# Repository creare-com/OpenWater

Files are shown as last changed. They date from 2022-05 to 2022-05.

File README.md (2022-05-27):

# OpenWater: A Citizen Science Water Quality Monitoring Platform
The goal of this project is to provide the bill of materials, design files, electronics, and firmware to allow you to build your own research grade turbidity meter. We hope that this work will help you to evaluate water quality in your local community through education or citizen science projects.

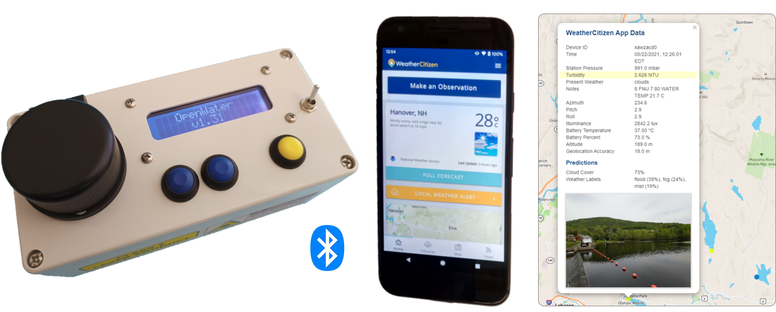
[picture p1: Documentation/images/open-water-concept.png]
OpenWater Turbidity Meter and Mobile Application


This project was supported by NOAA via SBIR contract WC133R18CN0057

## Assembly and Operation
For instructions on how to assemble, calibrate, and use the meter, see the [Documentation](https://github.com/creare-com/OpenWater/blob/master/Documentation).

## License
The Firmware is released under the BSD 3-Clause License.  The Hardware is released under the CERN Open Hardware License v2 - Permissive.  Use at your own risk.

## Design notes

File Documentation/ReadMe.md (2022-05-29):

## Documentation

**CAUTION! This project utilizes a laser diode. Read and follow all safety precautions.**

The R&D Report describes the design, validation, and testing of the turbidity meter during the project.

Follow the Assembly Instructions to build your own meter from the [parts list](https://github.com/creare-com/OpenWater/tree/main/Bill%20of%20Materials). Refer to the Operation Manual for calibration and safe operating instructions.

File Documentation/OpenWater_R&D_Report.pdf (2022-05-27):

OPENWATER – A CITIZEN SCIENCE MONITORING PLATFORM
Research & Development Report

### 1 INTRODUCTION

This report describes the research and development of the third-generation version of a research quality, relatively low-cost, open-source instrument for measurement of water turbidity in environmental samples. The device is shown in Figure 1.

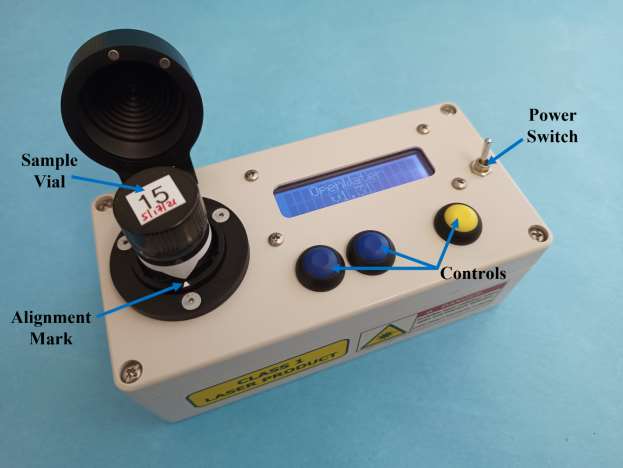
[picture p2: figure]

Figure 1. OpenWater Open-Source Turbidity Meter (3rd-Generation Design)

Principle of Operation. The OpenWater turbidity meter is composed of an 850 nm light source oriented at 90° to a light sensor which measures diffuse light scattered by turbidity in the sample. The infrared light source reduces the influence of sample color on turbidity measurements, and results are reported in Formazin Nephelometric Units (FNU). The meter was developed using guidance from Water Quality Standard ISO 7027 (Method c).

### 2 INSTRUMENT DESIGN

Design Overview. The core of the meter is the sample measurement well (Figure 2), which can be fabricated by 3D printing (stereolithography, SLA). The light source is a vertical cavity surface-emitting laser (VCSEL) with a total beam divergence angle (full-width at half intensity) of 4°. The VCSEL is operated in constant current mode to provide uniform light intensity for each measurement. The sensor is a light-intensity-to-frequency converter, which produces a square wave pulse output proportional to the incident light intensity. Pulses are counted during the integration period by a microcontroller which also controls the system.

The inner wall of the sample holder is corrugated to enhance absorption of stray light. A spring-plunger pushes the sample vial against PTFE guide rods in the wall to ensure consistent centering of the vial on the VCSEL. An alignment arrow on the top surface of the vial housing improves consistency of vial alignment. A miniature normally open reed switch placed in series with the laser is used as a safety interlock. A magnet is installed in the lid of the device to close the switch during operation, and the reed sensor is mounted in the sample holder opposite the magnet. Closing the lid actuates the reed switch, allowing the laser to be turned on by the microcontroller.

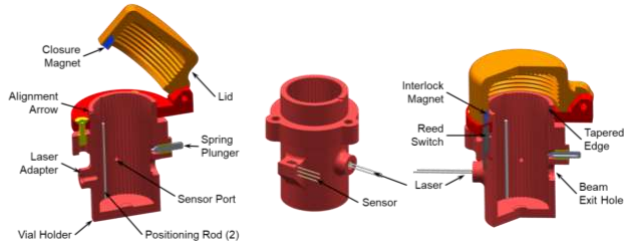
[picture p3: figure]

Figure 2. Turbidity Meter Optical System Design. The laser axis is arranged at 90° to the sensor view axis and both are normal to the vial axis. The sensor is mounted at the end of a narrow bore to minimize stray light (left); The light source and sensor are mounted directly on the outside of the sample holder (middle); The spring-plunger aligns the sample vial and laser centerlines (right).

Electronics. The VCSEL light source (TT Electronics, OPV332) is operated in constant current mode. The laser current source circuit is based on the LM-317 regulator, which has low cost, small component count, and stable current regulation. Figure 3 shows the laser control subsystem, including the laser, current regulator, reed switch safety interlock, and transistor interface to the microcontroller.

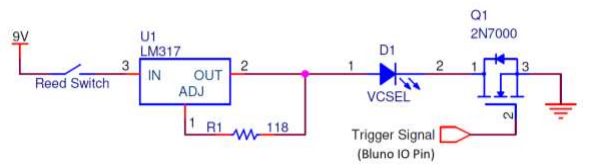
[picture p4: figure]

Figure 3. Laser Control Circuit Including Safety Interlock Reed Switch

The laser generates a repeatable signal at low turbidity values with a supply current of 10 mA. However, the voltage supplied by the microcontroller digital outputs is insufficient to drive this current. Therefore, the current source circuit is supplied with 9 V directly from the battery and the microcontroller digital output controls the laser via a 2N7000 transistor. The current source provides stable regulation with mean variability of 4.8 µA and drift between 22 and 50°C of only 0.5%.

The light-intensity-to-frequency converter (AMS, TSL237) only requires one 0.1 µF decoupling capacitor connected across the power supply. The sensor output is connected to an input pin of the 8-bit microcontroller with Bluetooth (Bluno ATmega328P, DFR0267, DFRobot) which controls the system. This board interfaces with an LCD module used for calibration and results display. Figure 4 shows the connections between the microcontroller and the low cost VCSEL and light sensor.

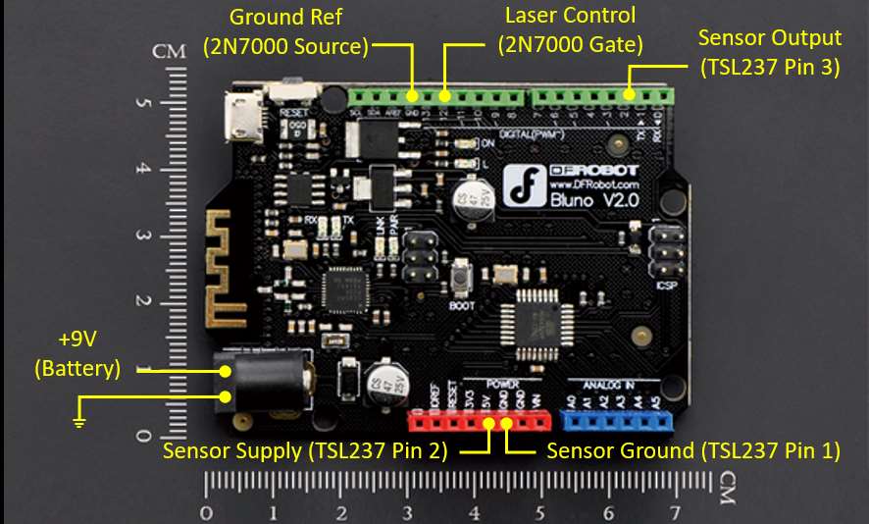
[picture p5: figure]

Figure 4. Bluno Microcontroller Connections to Light Source and Sensor

Enclosure. A commercial splash-resistant plastic enclosure (090816060, Rose Enclosures) is used for the third-generation prototype. The box measures 160 mm L x 80 mm W x 55 mm H (6.3 x 3.2 x 2.2 in.), providing ample space for the sample holder, microcontroller, LCD display, and battery pack. The lid of the enclosure is modified to accommodate the system components, as shown in the drawing in Figure 5. A piece of adhesive-backed Velcro (loop side) is installed on the inner wall of the enclosure base, opposite the laser beam exit hole in the vial holder. This simple, low-cost, absorptive material reduces the background count (light intensity measured at 0 NTU) by 30 percent and increases the ratio between counts at 0 and 20 NTU by 25 percent.

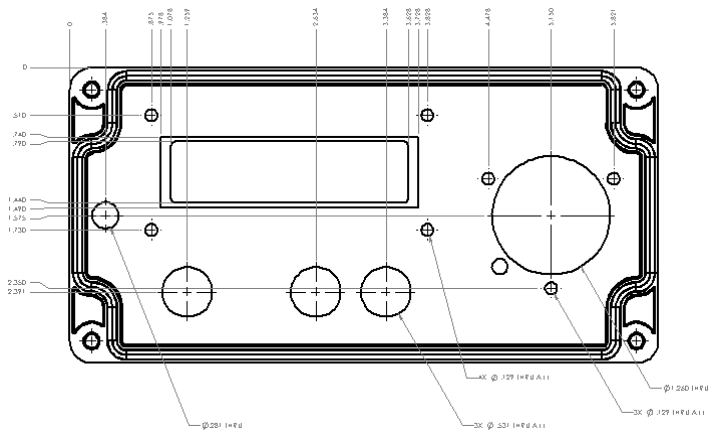
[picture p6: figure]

Figure 5. Modifications to the Commercial Enclosure

Safety. The turbidity meter contains a laser device that produces invisible radiation at 850 nm. If the laser is operated with a current greater than the recommended maximum (i.e., in an overcurrent failure mode at 30 mA), it will produce class 3B laser radiation. Class 3B devices have beams that are normally hazardous when a direct exposure occurs within Nominal Ocular Hazard Distance (NOHD). The IEC 60825-1 laser safety standard specifies an NOHD of several meters for class 3B devices.

There is no danger of harm due to the radiation from the laser in this instrument when it is used according to the instructions in the user manual. The following turbidity meter design features are meant to protect the user from potentially harmful infrared radiation:

- An interlock switch connected in series with the laser prevents operation while the lid is open.

- A warning label is placed over the seam of the enclosure to remind users not to open the enclosure while the device is powered on.
- The laser is operated in constant-current mode, below the recommended maximum current (<12 mA).
- The axis of the laser beam is oriented parallel to the base of the measurement well so that laser light is not directed towards the user.

Firmware. The OpenWater sensor uses an Arduino-type microcontroller with an integrated Bluetooth radio (Bluno, DFRobot). For the third-generation design, the system is controlled either by using buttons and an LCD display on the front panel, or via Bluetooth. In addition to the power switch, the front panel includes Up/Down buttons for scrolling through menus, and an Enter button for accepting settings (Figure 6). The calibration routine allows for selection of the integration time for each reading and the number of readings that are averaged for each measurement. The user can also select the value of each of the calibration points (typically 0 and 20 FNU).

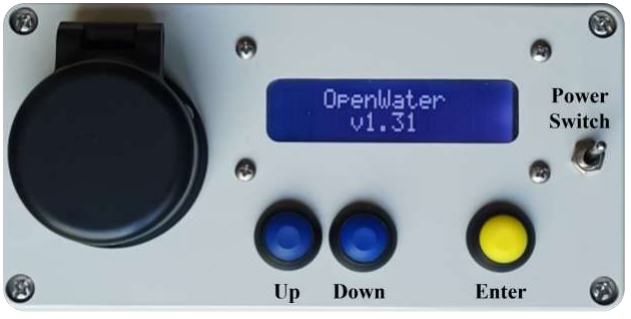
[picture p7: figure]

Figure 6. Front Panel Controls of the OpenWater Turbidity Meter

Bluetooth Low Energy service is included with the Bluno firmware. Table 1 shows the acceptable commands that control or request data from the device. These Bluetooth commands enable the mobile application to wirelessly execute turbidity measurements and calibrations.

Table 1. Turbidity Meter Commands (Firmware v1.31)
Command 00 | Description Execute Measurement | Data Returned (Format) None
01 | Read Last Reading Mean | Mean FNU (X.XX)
02 | Read Last Reading Std. Dev. | Std. Dev. FNU (X.XX)
03 | Read Number of Averages | Number (XX)
04 | Read Integration Time | Time (XX.X)
05 | Read Calibration Slope | FNU / Count (XXX.XX)
06 | Read Calibration Intercept | FNU (XXX.XX)
07 | Read Last Reading Mean Counts | Mean Counts (XXXX)
08 | Read Last Reading Std. Dev. Counts | Std. Dev. Counts (X.XX)
09 | Read All Parameters | See Note 1
10 | Read Stored Calibration Date | Unix Epoch Time
11<date> | Write Calibration Date | None
12<date> | Execute Calibration | None
14 | Read is Measuring Status Flag | Status (0 or 1)
Note 1: The “All Parameters” command returns a comma-separated string of values in the following order: Last Reading Mean, Last Reading Std. Dev., Number of Averages, Integration Time, Calibration Slope, Calibration Intercept, Mean Counts, Std. Dev. Counts, Calibration Date.

### 3 DATA SHARING

Mobile Application. A mobile device app called WeatherCitizen may be used for
OpenWater | device | control | and | data | dissemination | (described | in | detail | at
https://weathercitizen.org/). WeatherCitizen consists of a mobile application and a cloud database that enables collection and sharing of geolocated environmental measurement data. Measurements can be displayed on an interactive map in near real-time or downloaded by any user. Photographs and additional observations can be added to the data record to assist with interpretation by other users.

Figure 7 shows how the user navigates through the application to make a measurement with the OpenWater turbidity meter. First, the main menu allows the user to connect to an external device from a list of those available. Then, after selecting “Make an Observation” from the Home screen, the Snapshot button starts the process (at this point the application sends an Execute Measurement command). The application allows a photograph to be taken or added from storage, and various observations and notes can be recorded. Once all the metadata is provided, the observation is submitted. If the smartphone is not connected to the network, the observation is stored locally on the phone and uploaded to the remote WeatherCitizen database and web map display when connection is restored.

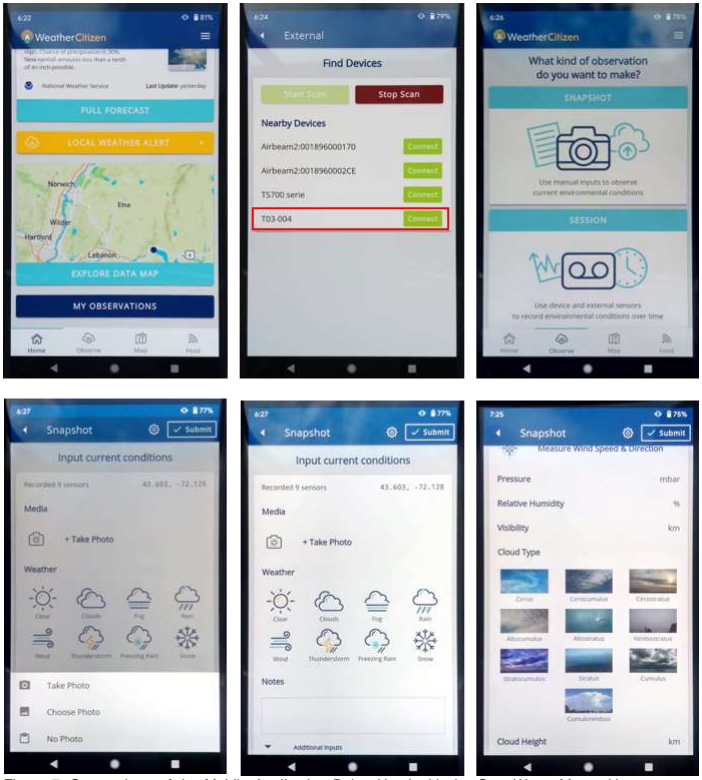
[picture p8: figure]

Figure 7. Screenshots of the Mobile Application Being Used with the OpenWater Meter: Home screen (upper left); Selecting a device to connect (upper center); Making an observation (upper right); Adding a photograph (lower left); Adding weather observations and notes (lower center); and Adding additional information (lower right).
Web-Based Data Repository. Sensor measurements collected using WeatherCitizen are stored in a web-based data repository. Several different background base map types, including street, satellite, contour, and nautical maps can be used to visualize data. Map symbols show the location of citizen observations, and they are color-coded based on the value of the underlying measurement parameter. Underlying data can be viewed in chart form (both time series and multi-variate scatter plots) or exported in CSV format for use by other software. In addition to turbidity measurements, the repository also incorporates data from other available sensors (weather, tides, and buoy-based water quality monitoring systems) allowing data from these fixed sensors to be viewed in conjunction with the citizen scientist observations. Figure 8 shows an example of a series of turbidity measurements that were collected along with water temperature, photographs, and weather observations from several water bodies in Enfield and Canaan, NH. In addition to selecting the parameter to display, the data and time range for observations can be adjusted.

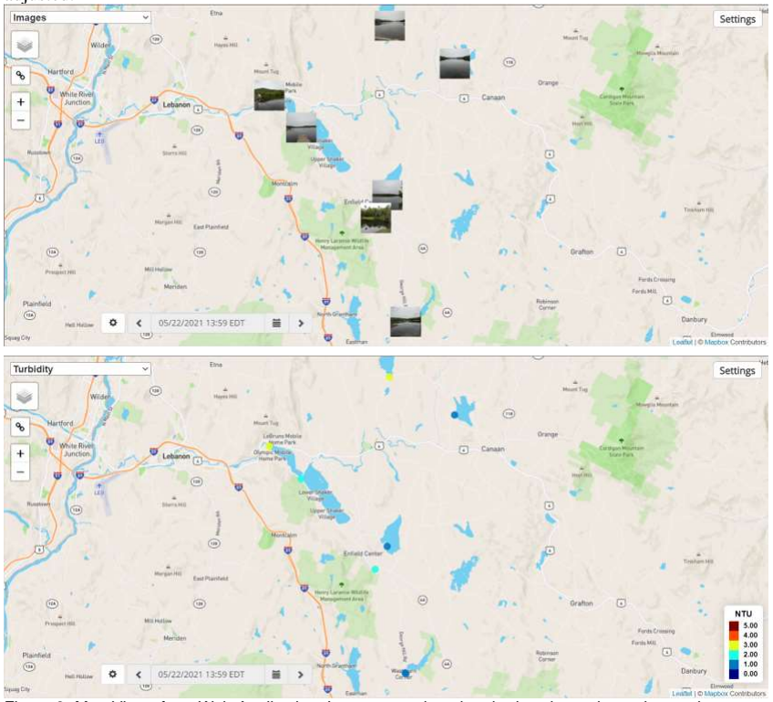
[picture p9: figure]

Figure 8. Map Views from Web Application: Images are pinned to the locations where observations were made (upper) and turbidity results that were measured at each site are displayed as dots with color scale indicating the magnitude of the measurement (lower).

Figure 9 shows the detail page that is displayed when the user selects one of the observation locations on the map. The page shows images and metadata associated with the observation.

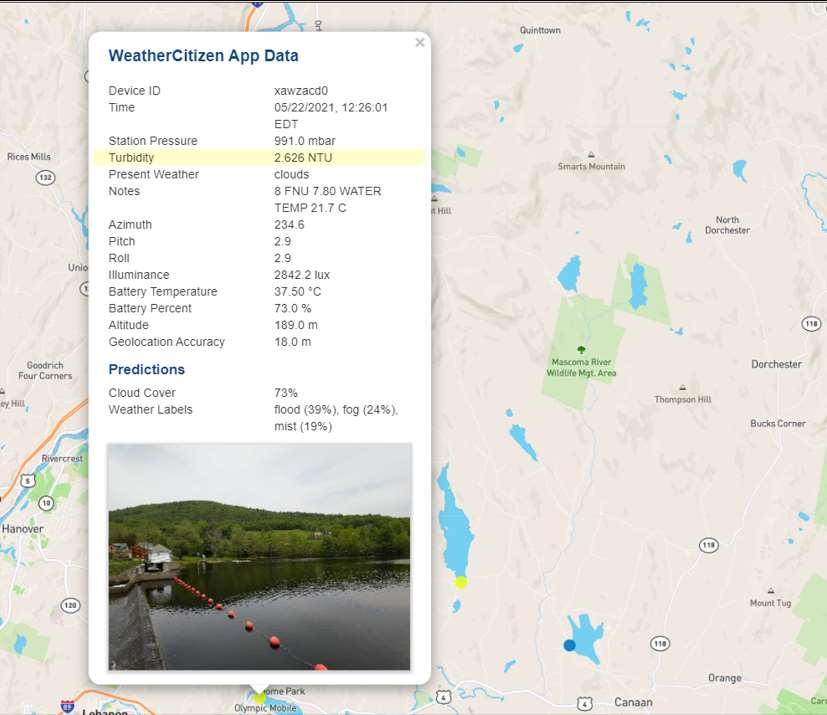
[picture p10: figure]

Figure 9. Observation Display Window in Web Application. Clicking on the map location of an observation opens the detail window.

### 4 CALIBRATION & VALIDATION

Measurement Units. A U.S. Geological Survey naming convention provides different turbidity units based on the design of the measurement instrument. Formazin Nephelometric Units (FNU) are used for meters having a monochromatic light source between 780–900 nm and with a detector placed at 90° to the incident beam. The more common Nephelometric Turbidity Units (NTU) and FNU have the same magnitude and are therefore comparable.

Calibration Procedure. The turbidity meter may be calibrated using liquid AMCO Clear primary calibration standards. Four sample vials are selected with similar background readings

(when filled with DI water) to create a matched set for calibration and sample measurement. Vials are filled with 0, 5, 8, and 20 FNU standards. Prior to each measurement, vials are gently inverted (not shaken) and carefully wiped using a lint-free cloth. The instrument measures light scattered from the 0 and 20 FNU vials and calculates a slope and offset for the calibration curve. Subsequent measurements are background corrected using the offset and quantified using the slope. Turbidity measurements at 0, 5, 8, and 20 FNU must fall within ±0.5 FNU of the true value to validate the calibration. The vial containing the 5 FNU standard is subsequently emptied and used for sample measurements and the 8 FNU standard is used for continuing calibration verification. The 0 and 20 FNU standards are retained for recalibration of the instrument in the field if necessary (for example, if a large drift due to high ambient temperature occurs). Settings and results of a typical calibration are shown in Table 2.

Table 2. Turbidity Meter T03-004 Initial Calibration

Calibration Values | 0, 20 FNU¹
Replicate Readings | 3
Integration Time | 3.0 Seconds
Mean Dark Counts | 6
Background Counts (0 FNU) | 826
Calibration Slope | 130 counts/FNU
Note: 1Formazin Nephelometric Units (FNU) are used for infra-red source meters.

Precision and Accuracy. The accuracy goal for the low-cost meter is ±0.5 FNU below 10 FNU and ±5% above 10 FNU. Results from 30 measurements of standards at 1 and 15 FNU in the laboratory and at 8 FNU in the field were analyzed, to make an estimate of instrument accuracy and precision (Table 3). The accuracy was calculated as the mean absolute deviation of the measurements as a percentage of the standard value. The uncertainty was calculated as the standard deviation of the measurements as a percentage of the mean measured value. These results demonstrate that the instrument accuracy was well within the target value of ±5% throughout the measurement range.

Table 3. Accuracy & Precision of Turbidity Standard Measurements

Standard Value | 1 FNU | 8 FNU | 15 FNU
Mean Absolute Deviation | 0.19 FNU | 0.15 FNU | 0.14 FNU
Mean Absolute Accuracy | 19% | 1.9% | 0.9%
Precision (Std. Deviation) | 0.04 FNU | 0.16 FNU | 0.12 FNU
Relative Uncertainty | 3.1% | 2.1% | 0.8%

Calibration Verification. After calibration, the linearity of the OpenWater meter was compared to that of a HACH 2100Q-IS in the range of 0–40. Serial dilutions of Formazin were prepared and measured on each device. The correlation coefficient of the linear regression equation was >0.999 in both cases (Figure 10). The small difference in offset between the two instruments was likely due to their individual calibrations.

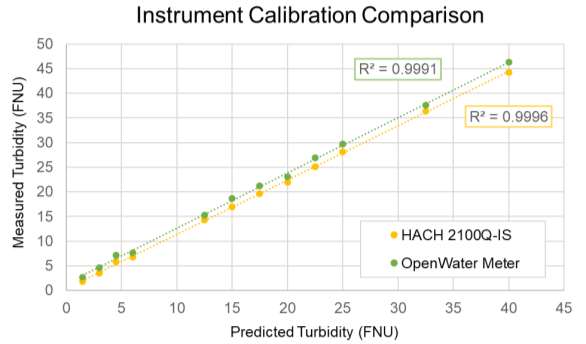
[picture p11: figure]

Figure 10. Laboratory Assessment of Instrument Linearity Using the OpenWater and HACH 2100Q-IS turbidity meters.

### 5 CASE STUDY

Long-term Comparison Study. Thirty samples were collected in October and November 2019 (almost daily) from Mascoma Lake in Enfield, New Hampshire. Sample turbidity was measured using the OpenWater and research-grade HACH instruments. Samples were collected from the town dock while it was present prior to its off-season removal (about half of the collection period) and by carefully wading to a depth of approximately 1 foot after it was removed. During each collection, a sample vial was filled and measured for water turbidity together with quality control samples using both meters. A 10 FNU standard (supplied by the manufacturer) was used as a calibration check for the 2100Q-IS meter, and all measurements fell between 9 and 11 FNU (±10%). An 8 FNU standard was used as a continuing calibration check for the OpenWater meter because it is closer in value to most of the environmental samples, and all measurements fell between 7.5 and 8.5 FNU (±0.5 FNU). Figure 11 shows data collected using both meters, and the ambient water temperature at the time of sample collection. The elevated turbidity results coincided with days on which significant wave action was observed. The measurement difference between the two meters does not appear to be related to the water sample temperature.

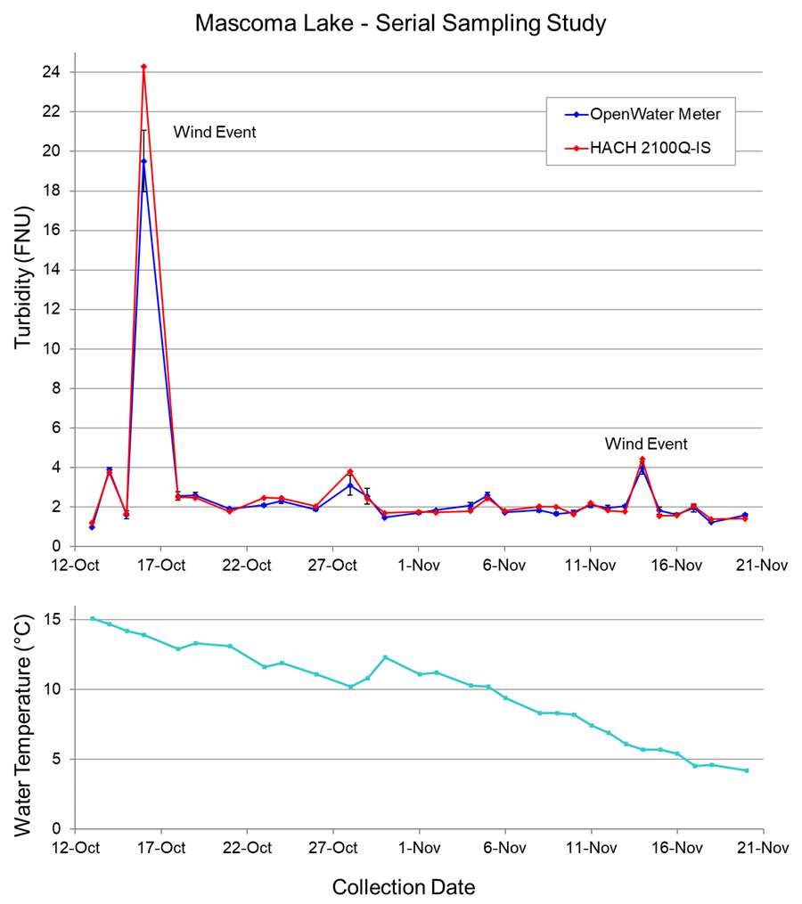
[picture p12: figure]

Figure 11. Turbidity Measurement Data Collected at Mascoma Lake Using the OpenWater and HACH Instruments. Error bars for OpenWater data represent the standard deviation of the 3 readings within each measurement.

Figure 12 shows the correlation between the two meters, with the ideal 1:1 relationship (solid blue line) and ±0.5 FNU bounds (dashed blue lines). The mean value of the absolute difference between the two meters was 0.05 FNU. Almost all measurements made with the OpenWater meter fell within ±0.5 FNU of the value measured with the 2100Q-IS meter.

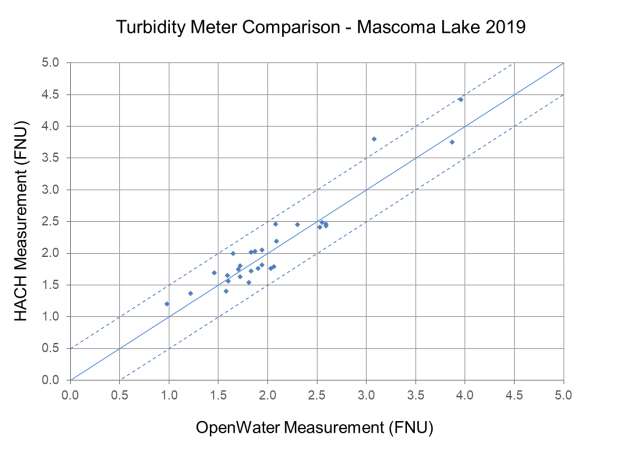
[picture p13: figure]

Figure 12. Correlation Between the OpenWater and HACH Turbidity Meters. A linear 1:1 relationship (solid line) and ±0.5 FNU deviation (dashed lines) are shown. The high result from October 16 was omitted for clarity.

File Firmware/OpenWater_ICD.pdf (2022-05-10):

## OpenWater Interface Control Document

June 2, 2021

BLUETOOTH LOW ENERGY INTERFACE

The open water electronics use a “Bluno” microprocessor board for the data collection and communication either with the attached LCD display or via Bluetooth.

The BLE service is part of the bluno firmware and I have not done anything to change it. The service has a UUID of: E6FBF347-C779-AE6F-E2DE-FCE9C0C1D49F and the characteristic dbf1 is used to communicate with the device. The following values are sent to command the device or request data from the device followed by a carriage return (0x0d). All data is currently returned as asci with a carriage return and linefeed after the data:

Value Sent | Description | Data Returned
0x00 | Collect Data | None
0x01 | Last Reading Mean | Mean FNU X.XX
0x02 | Last Reading StDev | StDev FNU X.XX
0x03 | Number of Averages | XX
0x04 | Integration Time | XX.X
0x05 | Calibration Slope | XXX.XX
0x06 | Calibration Intercept | XXX.XX
0x07 | Last Reading Mean Counts | Mean Cnts XXXX
0x08 | Last Reading StDev Counts | StDev Cnts X.XX
0x09 | All Parameters | See Below
0x10 | Read Stored Calibration Date | Unix Epoch Time
0x11 | Write Calibration Date | None – see below
0x12 | Initiate Calibration | None – use LCD
0x13 | Read Calibration Human Readable
0x14 | Read IsMeasuring | 0, 1

The all parameters command above returns the following string in comma separated decimal numbers with a carriage Return and Line Feed at the end:

<Last Reading Mean>, <Last Reading StDev>, <Number of Averages>, <Integration Time>, <Calibration Slope>, <Calibration Intercept>, <Mean Counts>, <StDev Counts>, <Calibration Date>

Writing the calibration time and asking for a calibration commands are as follows:

<command byte><date string><0d>

For example, to write a calibration date to the EEPROM you would send this following command for a date of 12345678:

0x11 0x31 0x32 0x33 0x34 0x35 0x36 0x37 0x38 0x0d

To request a calibration via the BLE interface, you would send the following (assuming the same date):

0x12 0x31 0x32 0x33 0x34 0x35 0x36 0x37 0x38 0x0d

The calibration is then completed using the LCD display.

NOTE: The code does a rudimentary check on the date string where if the string supplied is earlier than the calibration date stored in the EEPROM, the code will ignore the earlier date and take the EEPROM date and add one second to it and store than new value.

NOTE: If a calibration is initiated using the LCD and front panel buttons, the user is prompted to enter the calibration date and time and the verification described above is performed.

NOTE: The “Write Calibration Date” function (0x11) does no error checking of the date value, so you can reset the date to any value with that function. Use this power wisely.

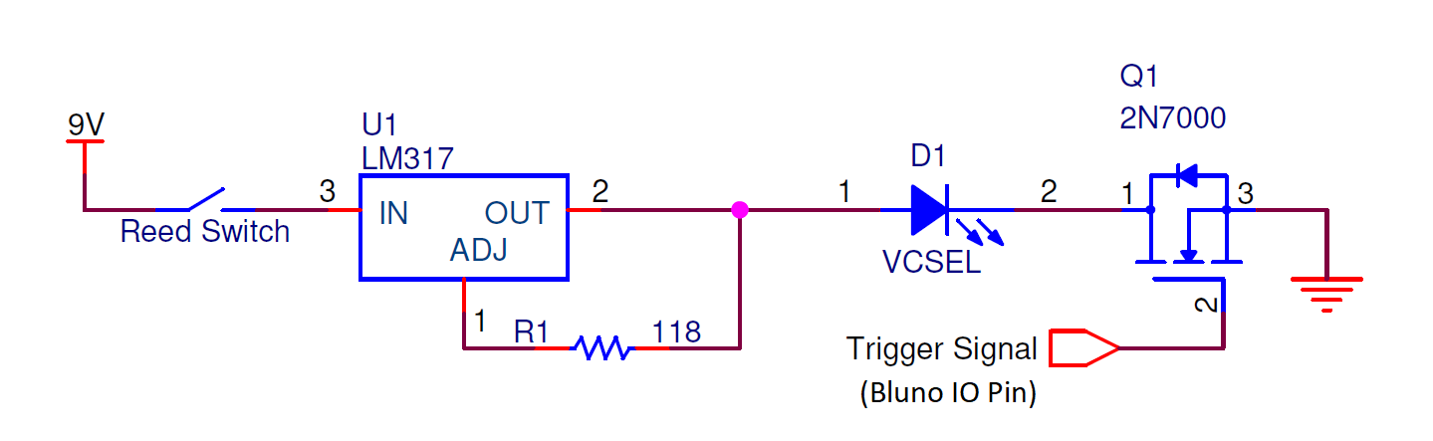
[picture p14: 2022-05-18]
Electronics/laser_control_schematic.png

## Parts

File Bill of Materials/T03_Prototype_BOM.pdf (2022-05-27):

OpenWater Turbidity Meter Prototype BOM and Cost Estimate
5/10/2022
Part Description | Manufacturer / Vendor | Part Number | UOM | Cost/UOM | Qty | Line Total
--- Parts ---
ABS Case, 6.3"L X 3.15"W | Rose Enclosures | 90816060 (https://www.digikey.com/product-detail/en/rose-enclosures/090816060/902-1354-ND/2300822) | ea | $18.80 | 1 | $18.80
Vial holder, hinge & lid (SLA) | Protolabs, Statasys | custom (3 parts) | set | $343.43 | 1 | $343.43
Light-to-frequency converter | AMS | TSL237S-LF (https://www.digikey.com/en/products/detail/ams/TSL237S-LF/3095041) | ea | $4.52 | 1 | $4.52
Capacitor - LFT decoupling, 100 uF | Kyocera AVX | TPSD107K010T0150V (https://www.digikey.com/en/products/detail/kyocera-avx/TPSD107K010T0150V/7567020?s=N4IgTCBcDaICwHYAcBaAjGsC3pQOQBEQBdAXyA) | ea | $1.21 | 1 | $1.21
Light source, VCSEL, 850 nm | TT Electronics | OPV332 (https://www.digikey.com/en/products/detail/tt-electronics-optek-technology/OPV332/761807?s=N4IgTCBcDaIPIAUBqBmFEC6BfIA) | ea | $6.11 | 1 | $6.11
Current source circuit - regulator | NTE Electronics | LM317T (https://www.digikey.com/en/products/detail/nte-electronics-inc/LM317T/11650484) | ea | $0.91 | 1 | $0.91
Current source circuit - resistor, 118 ohm | Yageo | MFR50SFTE52-118R (https://www.mouser.com/ProductDetail/Yageo/MFR50SFTE52-118R?qs=sGAEpiMZZMu61qfTUdNhG0IXHLFuiNndTeZ2zMGlekA%3D) | ea | $0.15 | 1 | $0.15
Power MOSFET, 60 V, 200 mA, TO-92 | onsemi | 2N7000 (https://www.digikey.com/en/products/detail/onsemi/2N7000/244278) | ea | $0.46 | 1 | $0.46
Reed switch | PIC GmbH | MS-210-3-1-0300 (https://www.digikey.com/product-detail/en/pic-gmbh/MS-210-3-1-0300/2010-1106-ND/9687363) | ea | $2.72 | 1 | $2.72
Magnet - interlock | McMaster-Carr | 5862K166 (https://www.mcmaster.com/5862k166) | ea | $0.45 | 2 | $0.90
Microcontroller w/ Bluetooth | DFRobot | DFR0267 (https://www.digikey.com/products/en?keywords=1738-1015-ND) | ea | $24.90 | 1 | $24.90
LCD display module | Adafruit | 772 (https://www.mouser.com/ProductDetail/Adafruit/772?qs=GURawfaeGuBo0m8%252B0bZ6%2Fg%3D%3D) | ea | $19.95 | 1 | $19.95
Battery holder | DFRobot | FIT0141 (https://www.digikey.com/en/products/detail/dfrobot/FIT0141/7597083) | ea | $2.50 | 1 | $2.50
Button | E-Switch | RP8100B2M1CEBLKBLUNIL (https://www.digikey.com/en/products/detail/e-switch/RP8100B2M1CEBLKBLUNIL/1785730?s=N4IgTCBcDaIKIHEAsBWA7ARgLQDkAiIAugL5A) | ea | $5.02 | 3 | $15.06
Switch | NKK Switches | M2011SD3W01 (https://www.digikey.com/en/products/detail/nkk-switches/M2011SD3W01/1049303?s=N4IgTCBcDaIMwDYAMBaOY4A4UDkAiIAugL5A) | ea | $4.07 | 1 | $4.07
Window | McMaster-Carr | 1227T759 (https://www.mcmaster.com/1227T759-1227T752/) | ea | $0.09 | 1 | $0.09
Hinge pin | McMaster-Carr | 90145A475 (https://www.mcmaster.com/90145A475/) | ea | $0.33 | 1 | $0.33
Spring plunger | McMaster-Carr | 8499A46 (https://www.mcmaster.com/8499a46) | ea | $6.96 | 1 | $6.96
PTFE rod, 0.070-in. diameter, 2-in long | McMaster-Carr | 84935K82 (https://www.mcmaster.com/84935K82/) | ea | $0.29 | 2 | $0.58
Brass press-fit insert, 6-32 thread, 1/4" long | McMaster-Carr | 92395A113 (https://www.mcmaster.com/92395A113/) | ea | $0.26 | 1 | $0.26
Brass press-fit insert, 4-40 thread, 1/4" long | McMaster-Carr | 92395A112 (https://www.mcmaster.com/92395A112/) | ea | $0.24 | 3 | $0.72
Hex standoff, female, 4-40 thread, 3/8" long | McMaster-Carr | 91115A509 (https://www.mcmaster.com/91115A509/) | ea | $2.55 | 4 | $10.20
Flat head screw, hex, 4-40 thread, 1/2" long | McMaster-Carr | 91263A503 (https://www.mcmaster.com/91263A503/) | ea | $0.29 | 3 | $0.86
Phillips head screw, 4-40 thread, 1/4" long | McMaster-Carr | 91735A104 (https://www.mcmaster.com/91735A104/) | ea | $0.09 | 4 | $0.37
Phillips head screw, 4-40 thread, 3/8" long, Nylon | McMaster-Carr | 94735A721 (https://www.mcmaster.com/94735A721-93135A275/) | ea | $0.09 | 4 | $0.34
--- Supplies ---
Batteries | Duracell | MN1500 (https://www.mouser.com/ProductDetail/Duracell/MN1500?qs=m04QHmkHpJLeqqMrP%252BjRQg%3D%3D) | ea | $0.55 | 6 | $3.30
Sample vials | Hach | 2434706 (https://ezvialz.com/spectrophotometer-cuvettes/814-hach-portable-turbidimeter-sample-cells-243706.html) | ea | $6.67 | 4 | $26.68
Turbidity standards | AMCO Clear | 8014 (https://www.gfschemicals.com/Product/amco-clear-turbidity-standard-10-ntu-item-8014-sku-85235) | 125 mL | $64.89 | 1 | $64.89
Total Cost Estimate | $561

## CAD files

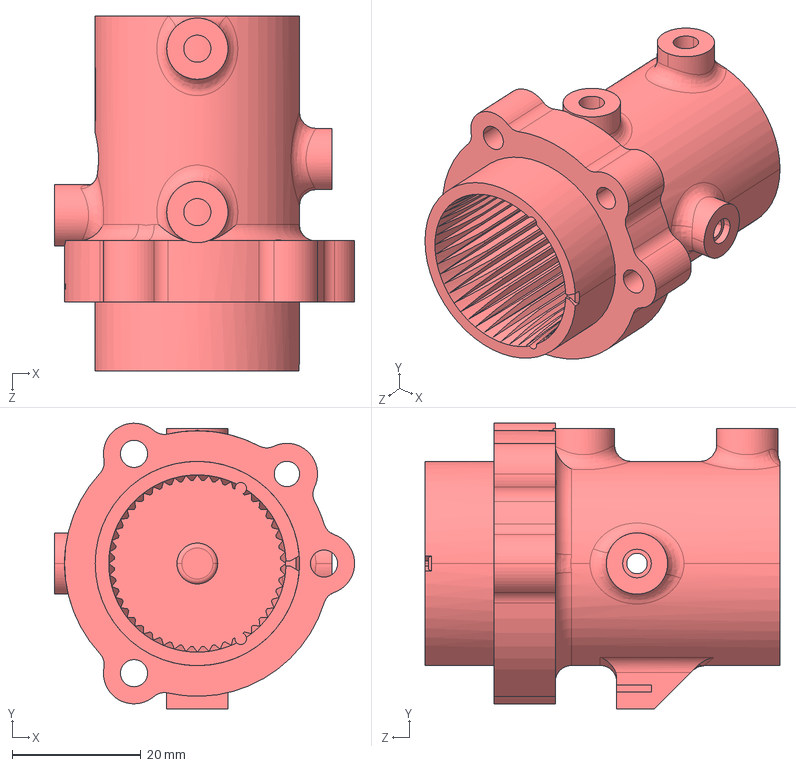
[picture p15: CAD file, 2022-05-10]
Mechanical/SLA-Sample-Well.STEP
46.7 x 44.4 x 55.2 mm

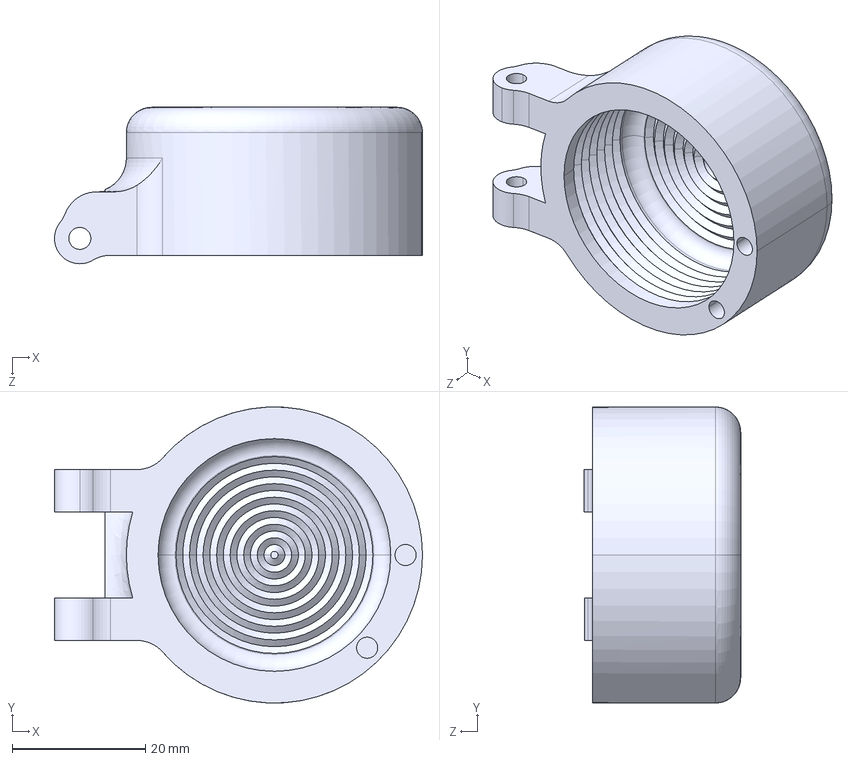
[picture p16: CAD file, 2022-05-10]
Mechanical/SLA-Sample-Well-Lid.STEP
55.2 x 44.4 x 23.5 mm

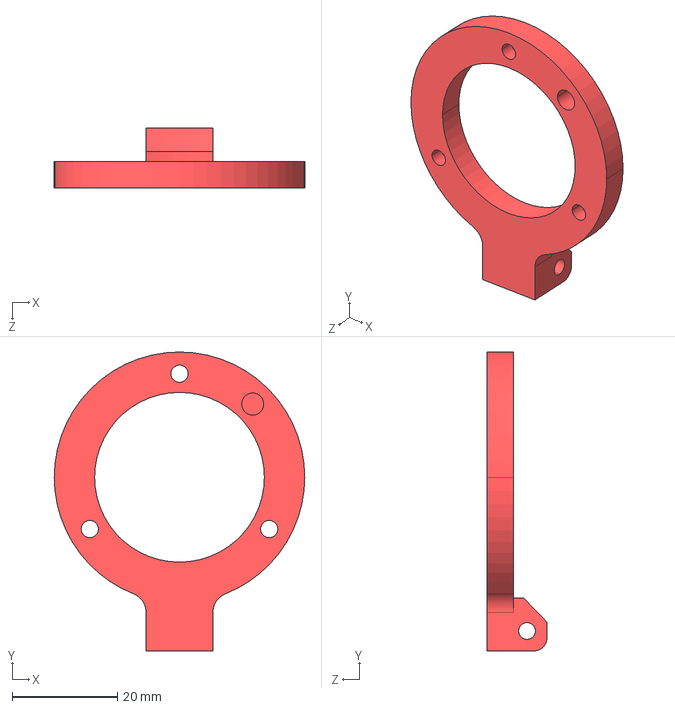
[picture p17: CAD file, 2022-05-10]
Mechanical/SLA-Sample-Well-Hinge.STEP
47.6 x 56.8 x 11.4 mm

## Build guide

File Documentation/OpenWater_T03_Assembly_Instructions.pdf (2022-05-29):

OPENWATER – A CITIZEN SCIENCE MONITORING PLATFORM
Turbidity Meter Assembly Instructions

### 1 INTRODUCTION

These instructions describe how to build the third-generation version of a research quality, relatively low-cost, open-source instrument for measurement of water turbidity in environmental samples. Refer to the R&D Report for a complete description of the design and validation of the instrument. Operating instructions are provided in the SOP. The completed device is shown in Figure 1.

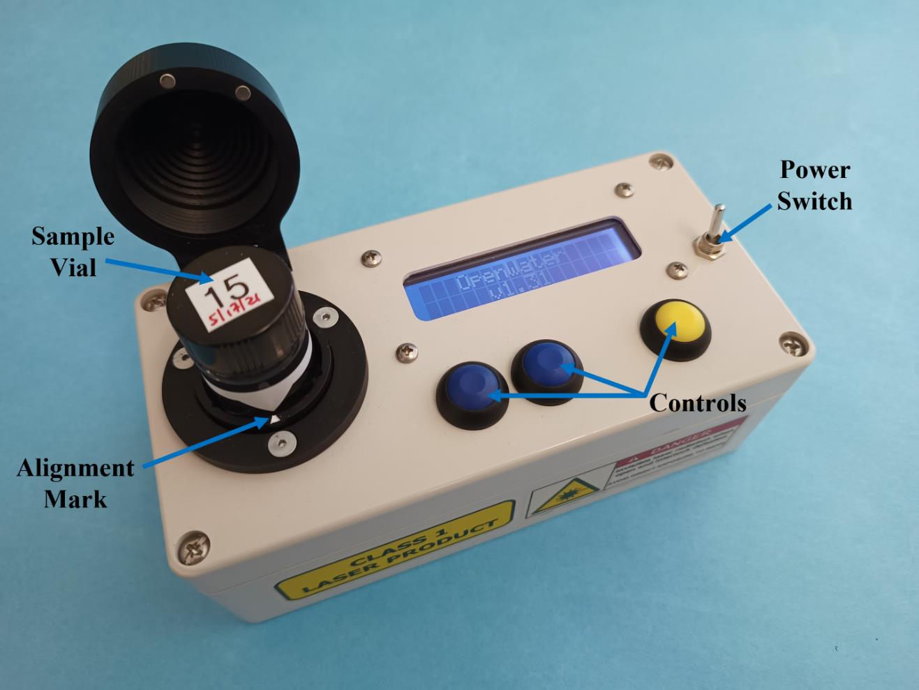
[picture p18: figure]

Figure 1. OpenWater Open-Source Turbidity Meter (3rd-Generation Design)

### 2 STEP 1: GATHER MATERIALS

The Bill of Materials lists everything that needs to be purchased to build the turbidity meter. To best reproduce the performance reported here, have the 3 components of the sample measurement well made by stereolithography (SLA), which is a high-fidelity method of 3D printing. For future development, other fabrication methods may be explored.

### 3 STEP 2: FABRICATION

### 3.1 ENCLOSURE

1. Machine the lid of the plastic case (Rose Enclosures, 090816060), following the drawing provided in the Mechanical folder and in Figure 2.

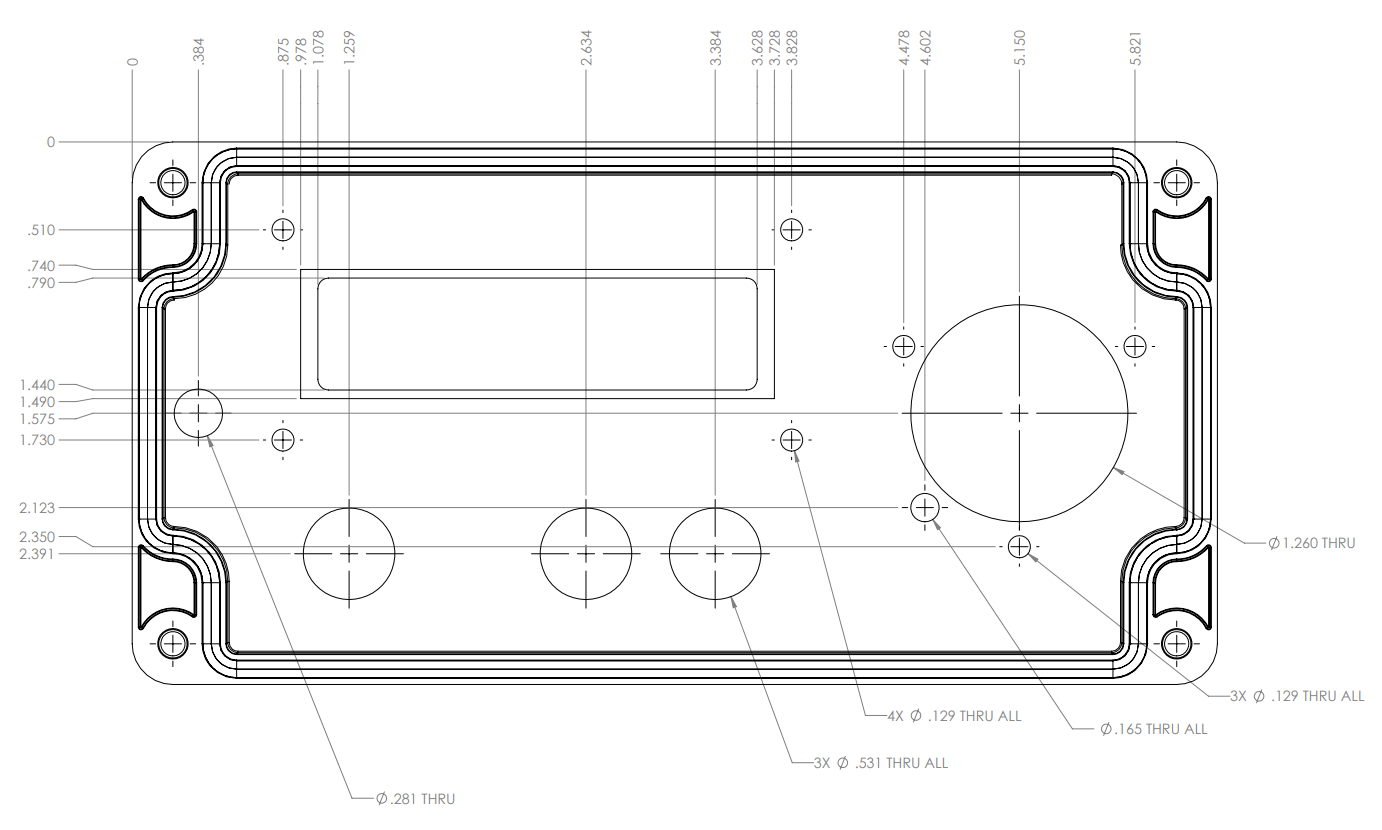
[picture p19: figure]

Figure 2. Modifications to the Commercial Enclosure

2. Cut a rectangular piece of 1/16-in. (1.6 mm) thick acrylic or polycarbonate sheet to 2.719 x 0.719 in. (69.1 x 18.3 mm). Round off the corners and glue the window to the case from the inside. The completed lid is shown in Figure 3.

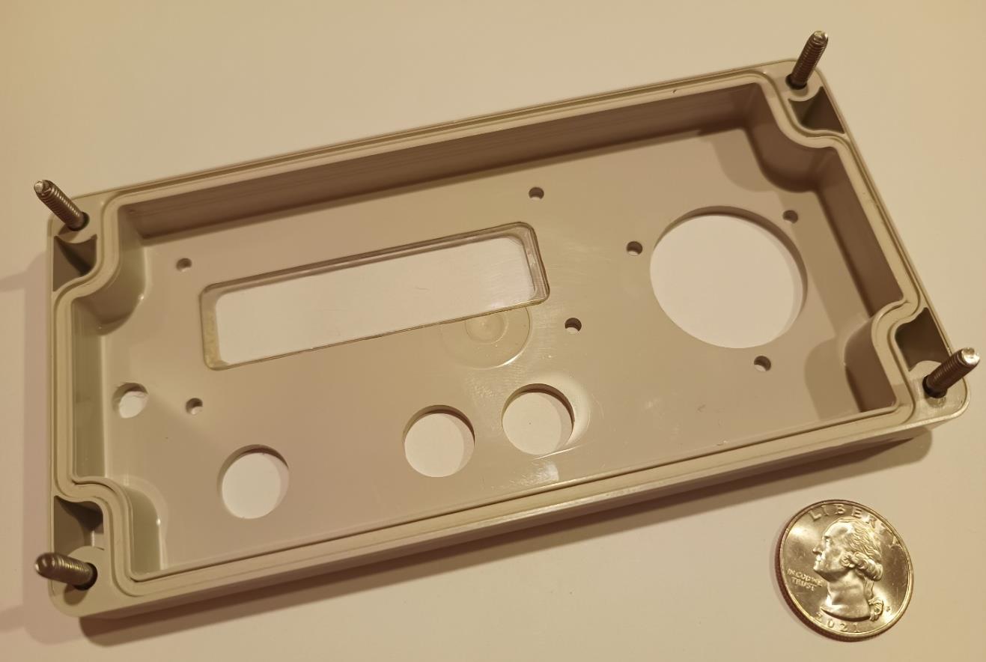
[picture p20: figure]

Figure 3. Machined Case Lid Assembled with Acrylic Window

### 3.2 ELECTRONICS

WARNING! Invisible laser radiation can cause eye damage. Avoid exposure to the beam.

The vertical cavity surface-emitting laser (VCSEL) produces invisible radiation at 850 nm. If the laser is operated with a current in excess of the recommended maximum (i.e., in an overcurrent failure mode at 30 mA) it will produce class 3B laser radiation. Class 3B devices have beams that are normally hazardous when a direct exposure occurs within Nominal Ocular Hazard Distance (NOHD). The IEC 60825-1 laser safety standard specifies an NOHD of several meters for class 3B devices.

WARNING! Do not energize the laser outside of an enclosure.

Do not operate the laser with more than 12 mA of current. Refer to the manufacturer data sheet and Application Note 221 in the Electronics folder for more information.

1. The laser control subsystem (Figure 4) is composed of the laser (OPV332, TT Electronics), current source (LM317 voltage regulator and 118-ohm ½-watt resistor), reed switch safety interlock (MS-210-3-1-0300, PIC GmbH), and transistor interface to the microcontroller (2N7000).

IMPORTANT! The reed switch interlock is critical to the safe operation of the instrument.

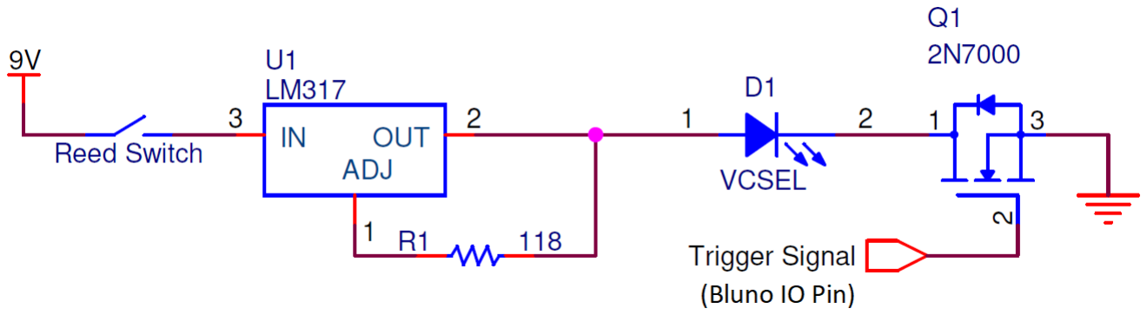
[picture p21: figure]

Figure 4. Laser Control Circuit Including Safety Interlock Reed Switch

Assemble the components using 26 AWG electrical wire, as shown in Figure 5. The distance between the pin connectors and the reed switch should be approximately 6.5 in. (165 mm). Terminate the microcontroller connection wires with square pin connectors. Insulate solder connections with heat-shrink tubing and cover the MOSFET and current source with an additional heat-shrink tubing jacket.

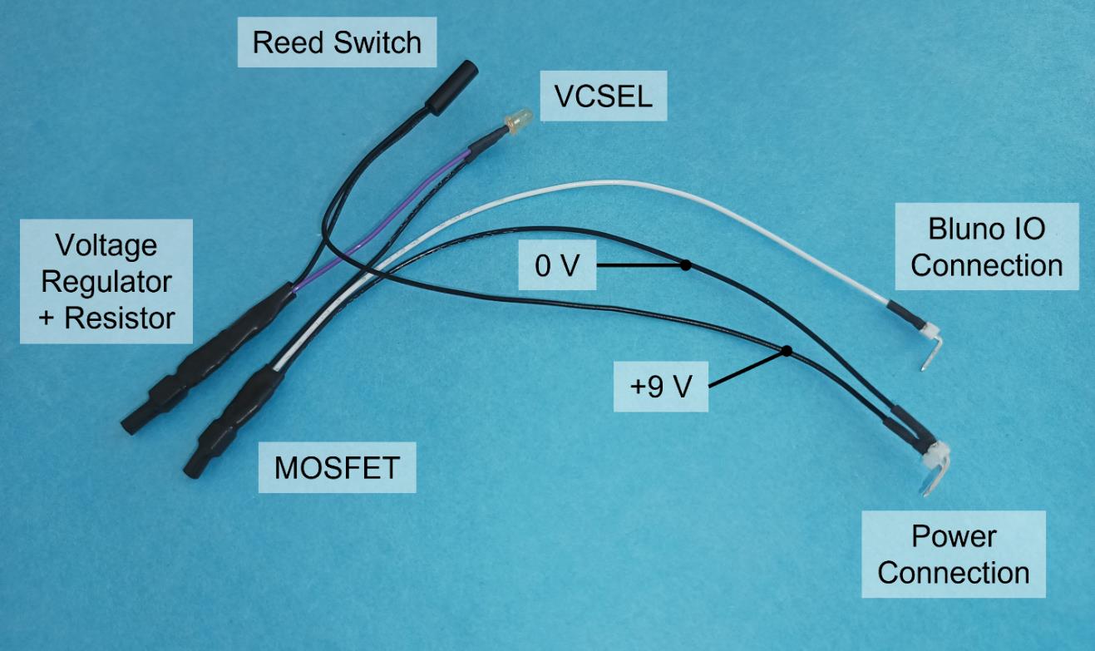
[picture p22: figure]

Figure 5. Assembled Laser Control Circuit

2. The light-to-frequency converter (TSL237, AMS) only requires one 0.1 µF decoupling capacitor connected across the power supply (refer to the data sheet in the Electronics folder). Solder a surface mount capacitor (e.g., TPSD107K010T0150V, Kyocera AVX) between pins 1 (GND) and 2 (VDD) of the converter, close to the body of the package (Figure 6). Space the capacitor far enough away from the plastic device package that

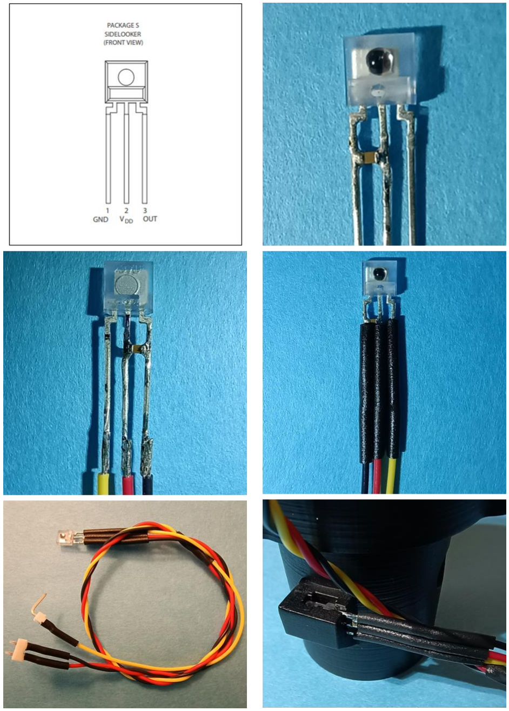
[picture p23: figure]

Figure 6. Light Sensor Circuit it will not interfere with installation of the sensor into the housing in the Sample Well. Connect 6 in. (150 mm) of 26 AWG electrical wire to each pin and terminate the wires with square pin connectors. Insulate solder connections with heat-shrink tubing and cover the LTF pins and capacitor with an additional heat-shrink tubing jacket.

3. The LCD shield (772, Adafruit) is supplied as a kit, including on-board pushbuttons for LCD control (Figure 7). The assembly instructions are in the Electronics folder or online at adafruit-16x2-character-lcd-plus-keypad-for-raspberry-pi.pdf. (https://cdn-learn.adafruit.com/downloads/pdf/adafruit-16x2-character-lcd-plus-keypad-for-raspberry-pi.pdf) Since the OpenWater meter has front panel buttons, the supplied pushbuttons do not need to be used. Instead, connect 26 AWG jumpers as shown in Figure 8, for connection to the case buttons in Step 4.4.3.

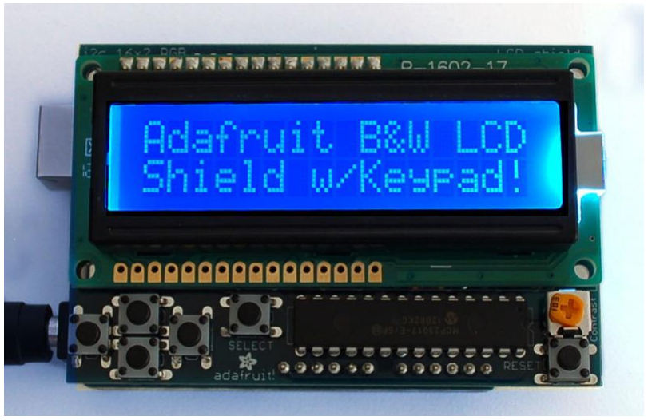
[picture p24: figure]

Figure 7. LCD Shield Completed Following Adafruit Instructions, with On-board Buttons

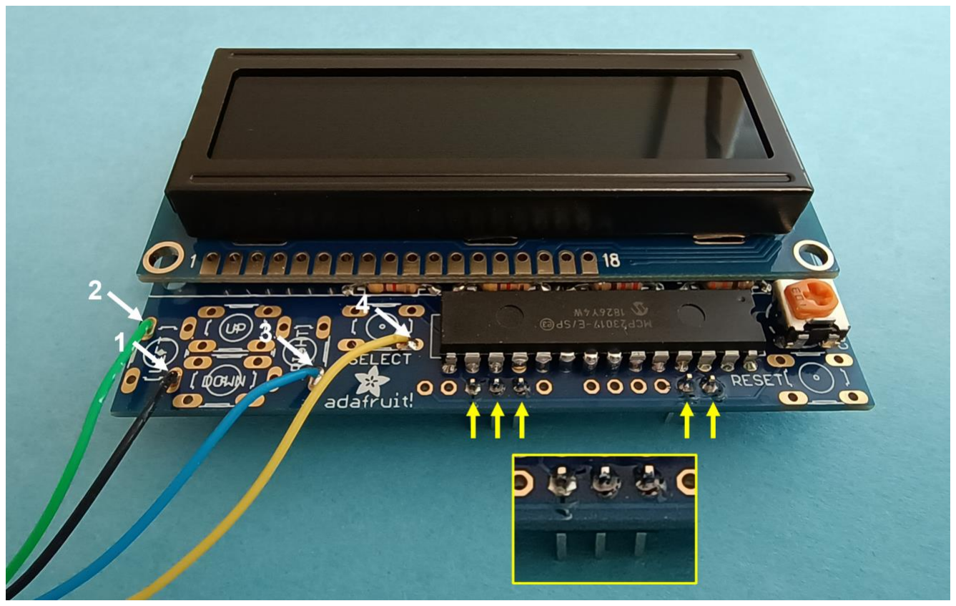
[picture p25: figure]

Figure 8. LCD Shield Assembly Modified for OpenWater, with Jumper Wires Installed

4. The battery holder (FIT0141, DFRobot) is supplied with a power jack that will fit the power connector of the Bluno microcontroller. Insert the toggle switch (M2011SD3W01, NKK Switches) into the positive wire of the power cable. Optionally, inline 2-pin connectors can be installed to simplify battery disconnection (Figure 9).

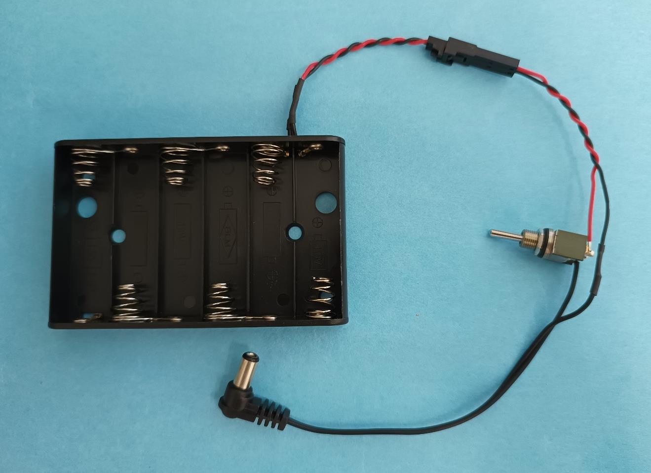
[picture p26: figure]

Figure 9. Battery Holder Assembly

### 4 STEP 3: PROGRAMMING & ASSEMBLY

### 4.1 BLUNO PROGRAMMING

1. If necessary, install the Arduino IDE on your computer.
2. Install the LCD Shield Library and Time Library (found in the Firmware folder) in the IDE.
3. Open the OpenWater-LCD-Firmware-v1.31.ino sketch in the IDE.
4. Using a USB cable, plug the Bluno into the computer.
5. In the IDE, select the correct port and device model.
6. Upload the sketch to the Bluno.
7. Follow the instructions in the DFRobot Bluetooth User Guide (in the Firmware folder) to rename the Bluetooth device using the “AT + NAME=” command. This will make it easier to identify your device when connecting via Bluetooth.

### 4.2 SAMPLE MEASUREMENT WELL

1. Press-fit three brass 4-40 threaded inserts into the mounting bosses of the Sample Well. Press-fit a brass 6-32 threaded insert into the spring-plunger boss in the sidewall of the Sample Well.
2. Thread the spring plunger into the boss in the sidewall of the Sample Well. Apply a dab of whiteout to the outer end of the plunger on one side (near the socket head) to make spring adjustments easier.
3. Press-fit two 1/8-in. diameter x 3/16-in. long magnets into the two holes in the rim of the Sample Well Lid. If they are loose, apply a drop of adhesive into the holes before pushing the magnets in, and allow to cure fully.
4. Place the Sample Well Hinge on the outside of the Case lid, and the Sample Well on the inside of the lid, each centered on the large round opening. Use three 4-40 x 1/2-in. flat-head screws to secure the three parts together, with the hinge closest to the top edge of the lid.
5. Assemble the Sample Well Hinge and Sample Well Lid, using the 1/8-in. x 1-in. dowel pin. If the pin is loose, apply a drop of adhesive to the bore of one side of the Sample Well Lid before assembly (push the dowel rod in from the opposite side, to avoid spreading adhesive into the bore of the Sample Well Hinge).
6. Slot the light-to-frequency sensor into the housing of the Sample Well, with the lens of the sensor facing inwards towards the center of the Well. Note that the capacitor will need to be attached correctly for the package to fit in the slot. Wrap the sensor and housing with black electrical tape to ensure a light-tight seal.
7. Push the VCSEL into the round counterbored hole in the sidewall, making sure it is completely seated in the housing. Apply a drop of adhesive over the joint between the VCSEL package and the housing to prevent it from shaking loose.
8. Cut two 2-in. long pieces of PTFE cord stock and insert them in the vertical grooves on the inner wall of the Sample Well.
9. Slide a sample vial into the Sample Well. The vial should slide down the two PTFE inserts, with the spring plunger gently pressing the vial against them. Adjust the spring pressure by screwing the body of the plunger in or out of the boss, until the vial is just barely retained when turned upside down (be careful not to drop the glass vial).

### 4.3 CASE BASE

1. Cut a 2-in. long piece of the loop side of 1-1/2-in. adhesive-backed Velcro strip. Install the material on the sidewall of the case on the upper left side.
2. Install the battery holder into the case base, in the upper right corner, using double-sided tape or adhesive.

### 4.4 CASE LID

1. Install the toggle switch into the hole on the far right-hand side of the case lid, with the “On” position oriented upwards (Figure 10).
2. Install the two blue push-button switches into the holes in the bottom-center of the case lid. Install the yellow push-button switch into the remaining hole (Figure 10).

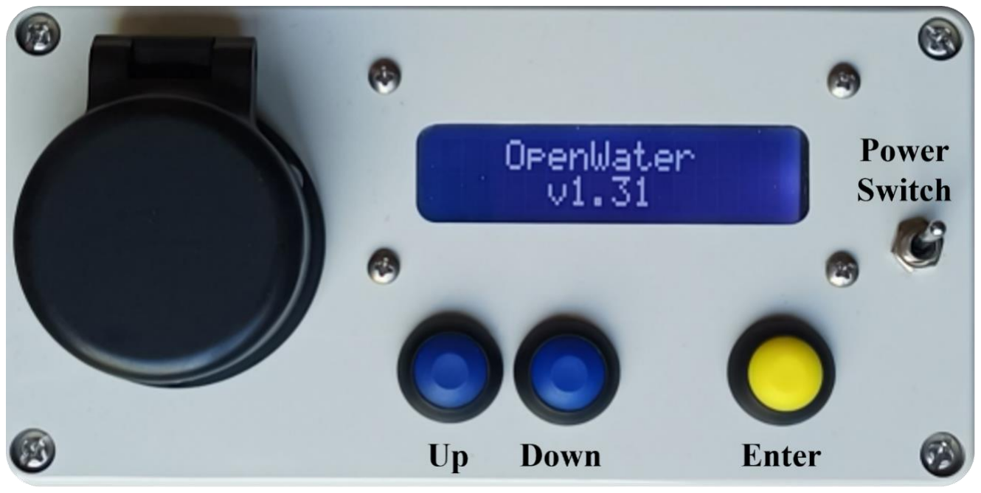
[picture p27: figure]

Figure 10. Front Panel Controls of the OpenWater Turbidity Meter

3. Connect one terminal of each push-button switch together in series using 26 AWG wire. Connect one end of the series to the LCD shield using the black wire (1) in Figure
8. Connect the remaining terminal of the ‘Up” button to the green wire (2), the “Down” button to the blue wire (3), and the “Select” button to the yellow wire (4) on the shield.
4. Using four 4-40 x 1/4-in. Phillips-head screws, install the four 3/8-in. long hex standoffs to the inside of the case lid around the perimeter of the window. Install the LCD shield onto the standoffs with the screen facing the clear window in the case lid, using four Nylon 4-40 x 3/8-in. Phillips-head screws.
5. Plug the pins of the VCSEL control circuit and the light sensor into the Bluno board at the locations shown in Figure 11. Plug the Bluno board into the LCD shield and secure them together using a zip tie. Plug the power connector from the battery pack into the power jack of the Bluno.
6. Tuck all loose wires in between the circuit boards and the edge of the case lid (Figure 12). Secure with zip ties as needed.

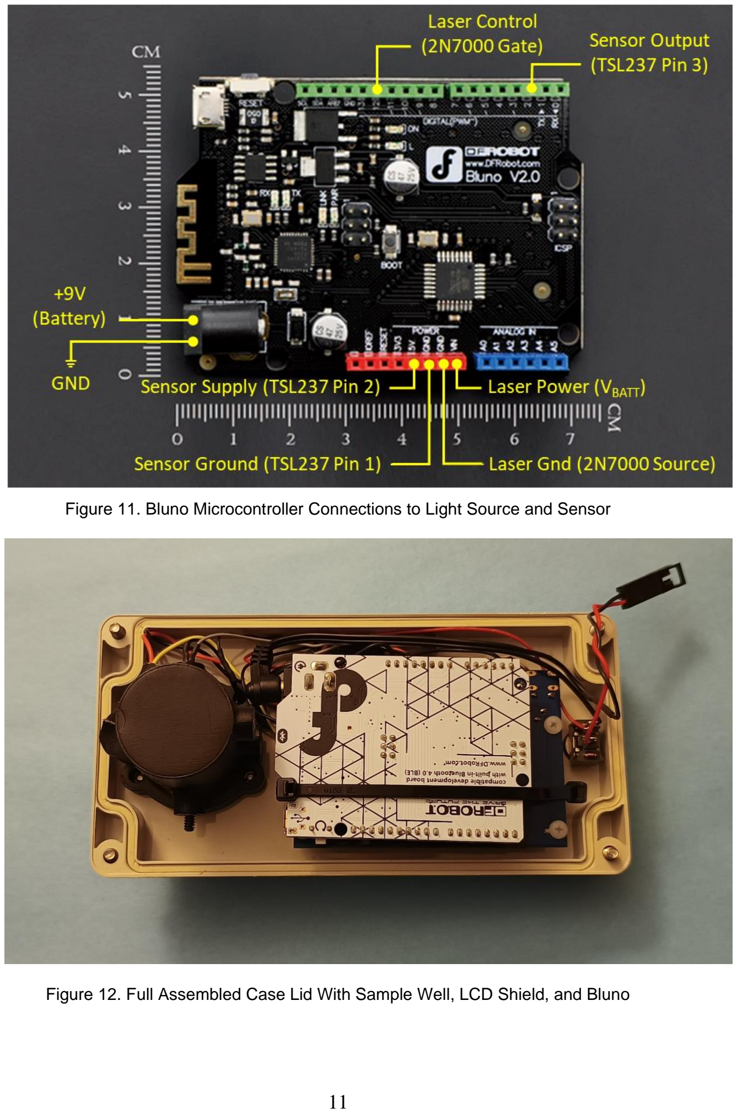
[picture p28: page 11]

Figure 11. Bluno Microcontroller Connections to Light Source and Sensor

Figure 12. Full Assembled Case Lid With Sample Well, LCD Shield, and Bluno

### 4.5 BATTERY INSTALLATION

WARNING! Do not energize the laser with the case open.

1. Make sure the VCSEL is securely installed in the Sample Well.
2. Make sure the power switch is off.
3. Install the batteries (6 x AA) into the holder.
4. Close the case and fasten with the four screws provided.

### 4.6 INSTRUMENT LABELING

1. Print the labels provided in the Documentation folder, on 1-in. x 2-5/8-in. polyester labels.
2. Place the Class 1 Laser label (Figure 13, left) on the outside of the case. Locate it on the left side of the front sidewall of the case (Figure 1).
3. Place the Danger label (Figure 13, center) on the outside of the case. Locate it on the right side of the front sidewall of the case (Figure 1).
4. Place the Warning label (Figure 13, right) on the outside of the case. Locate it over the seam (between case base and lid) on the rear sidewall of the case.

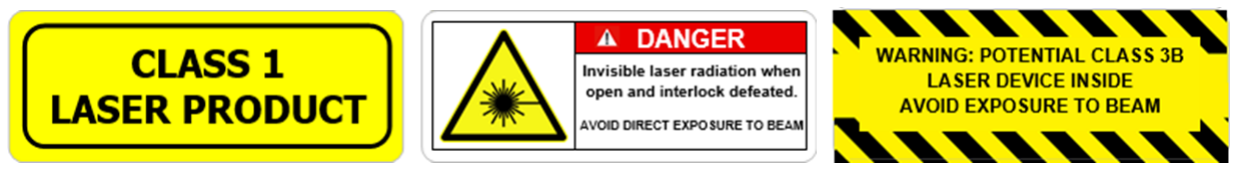
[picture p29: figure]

Figure 13. Safety Labels for Turbidity Meter Case

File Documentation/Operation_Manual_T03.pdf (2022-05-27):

Open-Source Turbidity Meter Operation Manual – Hardware Build T03

### 1 DESIGN OVERVIEW

The turbidity meter is composed of an 850 nm light source oriented at 90° to a light sensor which measures diffuse light scattered by turbidity in the sample. The infrared light source reduces the influence of sample color on turbidity measurements, and results are reported in formazin nephelometric units (FNU). The meter was developed using guidance from Water Quality Standard ISO 7027 (method c).

The light source is a vertical cavity surface-emitting laser (VCSEL, TT Electronics OPV332) with a total beam divergence angle (full-width at half intensity) of 4°. The VCSEL is operated in constant current mode to provide uniform light intensity for each measurement.

The sensor is a light-intensity-to-frequency converter (AMS TSL237), which produces a square wave pulse output proportional to the incident light intensity. Pulses are counted during the integration period by a microcontroller which also controls the system.

The inner wall of the sample holder is corrugated to enhance absorption of stray light. A spring-plunger pushes the sample vial against PTFE guide rods in the wall to ensure consistent centering of the vial on the VCSEL axis (Figure 1).

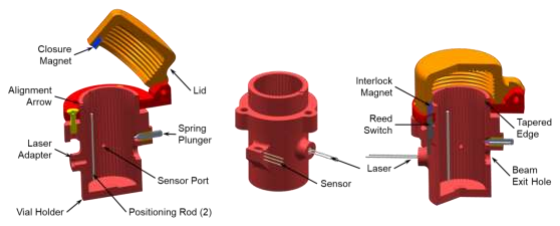
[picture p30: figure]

Figure 1. Turbidity Meter Optical System Design. The laser axis is arranged at 90° to the sensor view axis and both are normal to the vial axis. Left) The sensor is mounted at the end of a narrow bore to minimize stray light; Middle) The light source and sensor are mounted directly on the outside of the sample holder; Right) The spring-plunger aligns the sample vial and laser centerlines.

Operation Manual for Build T03 May 29, 2019

### 2 SAFETY

WARNING! Invisible laser radiation can cause eye damage. Avoid exposure to the beam.

The turbidity meter contains a laser device that produces invisible radiation at 850 nm. If the laser is operated with a current in excess of the recommended maximum (i.e. in an overcurrent failure mode at 30 mA) it will produce class 3B laser radiation. Class 3B devices have beams that are normally hazardous when a direct exposure occurs within Nominal Ocular Hazard Distance (NOHD). The IEC 60825-1 laser safety standard specifies an NOHD of several meters for class 3B devices.

When used according to these instructions there is no danger of harm due to the radiation from the laser. The following turbidity meter design features are meant to protect the user from potentially harmful infrared radiation:

- An interlock switch connected in series with the laser prevents operation while the lid is open.
- A warning label is placed over the seam of the enclosure to remind users not to open the enclosure while the device is powered on.
- The laser is operated in constant-current mode, below the recommended maximum current (<12 mA). When operated at this power, the laser presents a Class 3R or 1M laser eye hazard (see TT Electronics Application Bulletin 221). (https://www.ttelectronics.com/TTElectronics/media/ProductFiles/ApplicationNotes/App-Note-221-Laser-Safety-Bulletin.pdf)
- The axis of the laser beam is oriented parallel to the base of the measurement well so that laser light is not directed towards the user.

IMPORTANT! Follow these directions for safe operation:

1. Make sure that the lid of the measurement well is closed when making measurements.
2. Do not operate the instrument with the bottom of the case removed.
3. Turn off the power to the instrument when changing the batteries.
4. Do not remove the laser from the housing, apply a different power source, or defeat the interlock switch.
5. Do not place a reflective object into the measurement well.
6. Do not look directly into the laser beam.

### 3 INSTRUMENT OPERATION

The features and controls of the instrument are shown in Figure 2. Sample vials are inserted into the measurement well and rotated to align the mark on the vial with the arrow on the edge of the well. The lid must be closed in order to operate the instrument correctly.

Measurements of sample turbidity are made using the following procedure:

1. Turn on the power and wait for “Open Water” to appear on the screen.
2. Press the yellow Enter button to access the menu.
3. Swirl the water sample thoroughly to ensure it is well mixed (without entraining air bubbles).
4. Use small aliquots of sample to rinse the sample vial, and then fill the vial to the shoulder with sample.
5. Wipe the outer surface of the sample vial with a clean, soft cloth.
6. Insert the vial into the measurement well with the white arrow on the vial aligned with the arrow marked on the rim of the well.
7. Close the lid. The laser will not operate with the lid open.
8. Press Enter to continue.
9. Measurement progress and the final result are displayed on the screen.
10. The measured turbidity value and the standard deviation of the readings are shown in FNU.

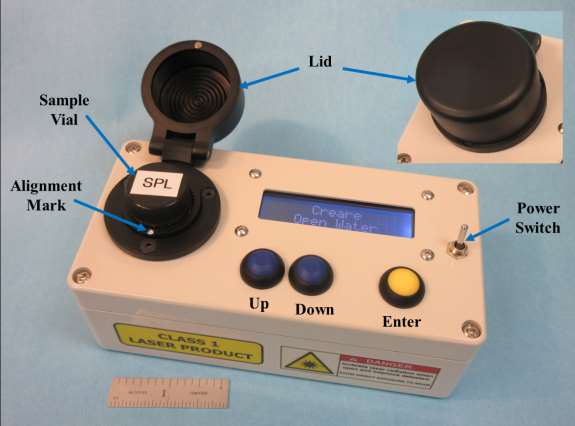
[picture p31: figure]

Figure 2. Prototype Turbidity Meter.

### 4 CALIBRATION PROCEDURE

The instrument must be calibrated prior to measurement of samples. The calibration can be checked before sample measurement using the 8 NTU standard. In case the check standard does not fall within the acceptable range (7.5-8.5 NTU), the calibration can be repeated in the field with the following steps:

1. Turn on the power and wait for “OpenWater” to appear on the screen.
2. Press the yellow Enter button to access the menu.
3. Press the blue Down (right-hand) button to select “Calibrate”.
4. Press the Enter button.
5. The “Print Counts” setting is displayed.
6. Press the blue Up (left-hand) button to choose No, or the Down button to select Yes.
7. Press Enter to continue.
8. The “Number of Averages” setting is displayed.
9. Use the Up and Down buttons to select the desired number.
10. Press Enter to continue.
11. The “Integration Time” setting is displayed.
12. Use the Up and Down buttons to select the desired time.
13. Press Enter to continue.
14. The “First Solution Concentration” setting is displayed.
15. Use the Up and Down buttons to select the desired concentration.
16. Wipe the outer surface of the 0 NTU vial with a clean, soft cloth.
17. Insert the vial into the measurement well with the white arrow on the vial aligned with the arrow marked on the rim of the well.
18. Close the lid. The laser will not operate with the lid open.
19. Press Enter to continue.
20. The “Second Solution Concentration” setting is displayed.
21. Use the Up and Down buttons to select the desired concentration.
22. Wipe the outer surface of the 20 NTU vial with a clean, soft cloth.
23. Insert the vial into the measurement well with the white arrow on the vial aligned with the arrow marked on the rim of the well.
24. Close the lid. The laser will not operate with the lid open.
25. Press Enter to continue.

26. The display will return to the menu.

Note: The Print Counts setting can be changed without changing the calibration. After selecting the desired value (Yes or No), press Enter and power off the device. The new display setting will be saved for subsequent measurements.

### 5 SMARTPHONE APPLICATION

The turbidity meter leverages the power of an open-source framework called WeatherCitizen (https://weathercitizen.org/). It consists of a mobile application and a cloud database that enables collection and sharing of geolocated environmental measurement data. Measurements can be displayed on an interactive map in near real-time or downloaded by any user (Figure 3). Photographs and additional observations can be added to the data record to assist with interpretation by other users.

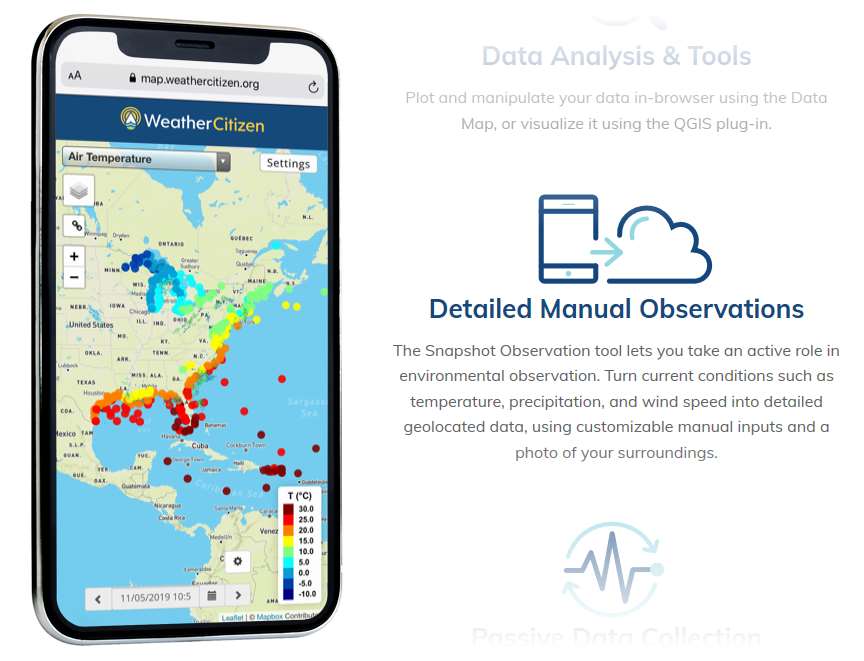
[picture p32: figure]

Figure 3. WeatherCitizen Mobile Application.

The turbidity meter can be used with the WeatherCitizen application with the following steps:

1. Download and install the latest version of WeatherCitizen from the Google Play Store (Android OS) or the Apple App Store (iOS).
2. Turn on BlueTooth in your phone Settings.
3. Open the WeatherCitizen application and connect to the turbidity meter:
a. Turn on the turbidity meter.
b. Tap Menu (≡) > Connect External Sensors > Start Scan.
c. Tap the Connect button next to the turbidity meter (the device name will be the serial number of the meter). A WaterMonitor device should now be listed under Connected Devices, with Creare as the manufacturer.
d. Tap the back arrow () to return to the application.
4. Place a water sample into the measurement well and close the lid.
5. Tap on Make an Observation > Snapshot. The meter will automatically make a turbidity measurement.
6. Choose to take a photo, select an existing photo, or not add a photo to the observation.
7. Add information to the observation, such as weather conditions and notes.
8. Tap the Submit button. Review the observation data for accuracy.

The turbidity meter can be calibrated from WeatherCitizen with the following steps:

1. Place the low standard (usually 0 FNU) into the measurement well and close the lid.
2. Connect to the turbidity meter by following step 3 above.
3. Calibrate the turbidity meter:
a. Tap Menu (≡) > Calibrate Sensors.
b. Scroll down to the WaterMonitor heading, tap the Calibrate button, and confirm.
c. Follow the prompts on the turbidity meter to complete the calibration.
d. Tap OK and check that the Last Calibrated field was updated correctly.
e. Tap the back arrow () to return to the application.

### 6 DEFAULT SETTINGS

The following default values were set before instrument delivery:

- Low calibration standard: 0 NTU
- High calibration standard: 20 NTU
- Number of readings per measurement: 3
- Integration time: 3 seconds
- Show individual results: No

### 7 BATTERY REPLACEMENT

CAUTION! Avoid exposure to laser radiation while the device is disassembled.

Batteries will need replacement after approximately 30 hours of operation. Please read the safety information provided in Section 2.

1. Make sure that the power switch is OFF.
2. Carefully cut through the label connecting the two halves of the enclosure. Doing so indicates that you accept responsibility for laser radiation safety.
3. Unscrew the fasteners at each corner of the top panel (they are captive screws and will not fall out).
4. Move the top panel to one side, being careful not to damage the electrical wires connected to the battery.
5. Remove and replace the batteries.
6. Replace the top panel and retighten the four screws.

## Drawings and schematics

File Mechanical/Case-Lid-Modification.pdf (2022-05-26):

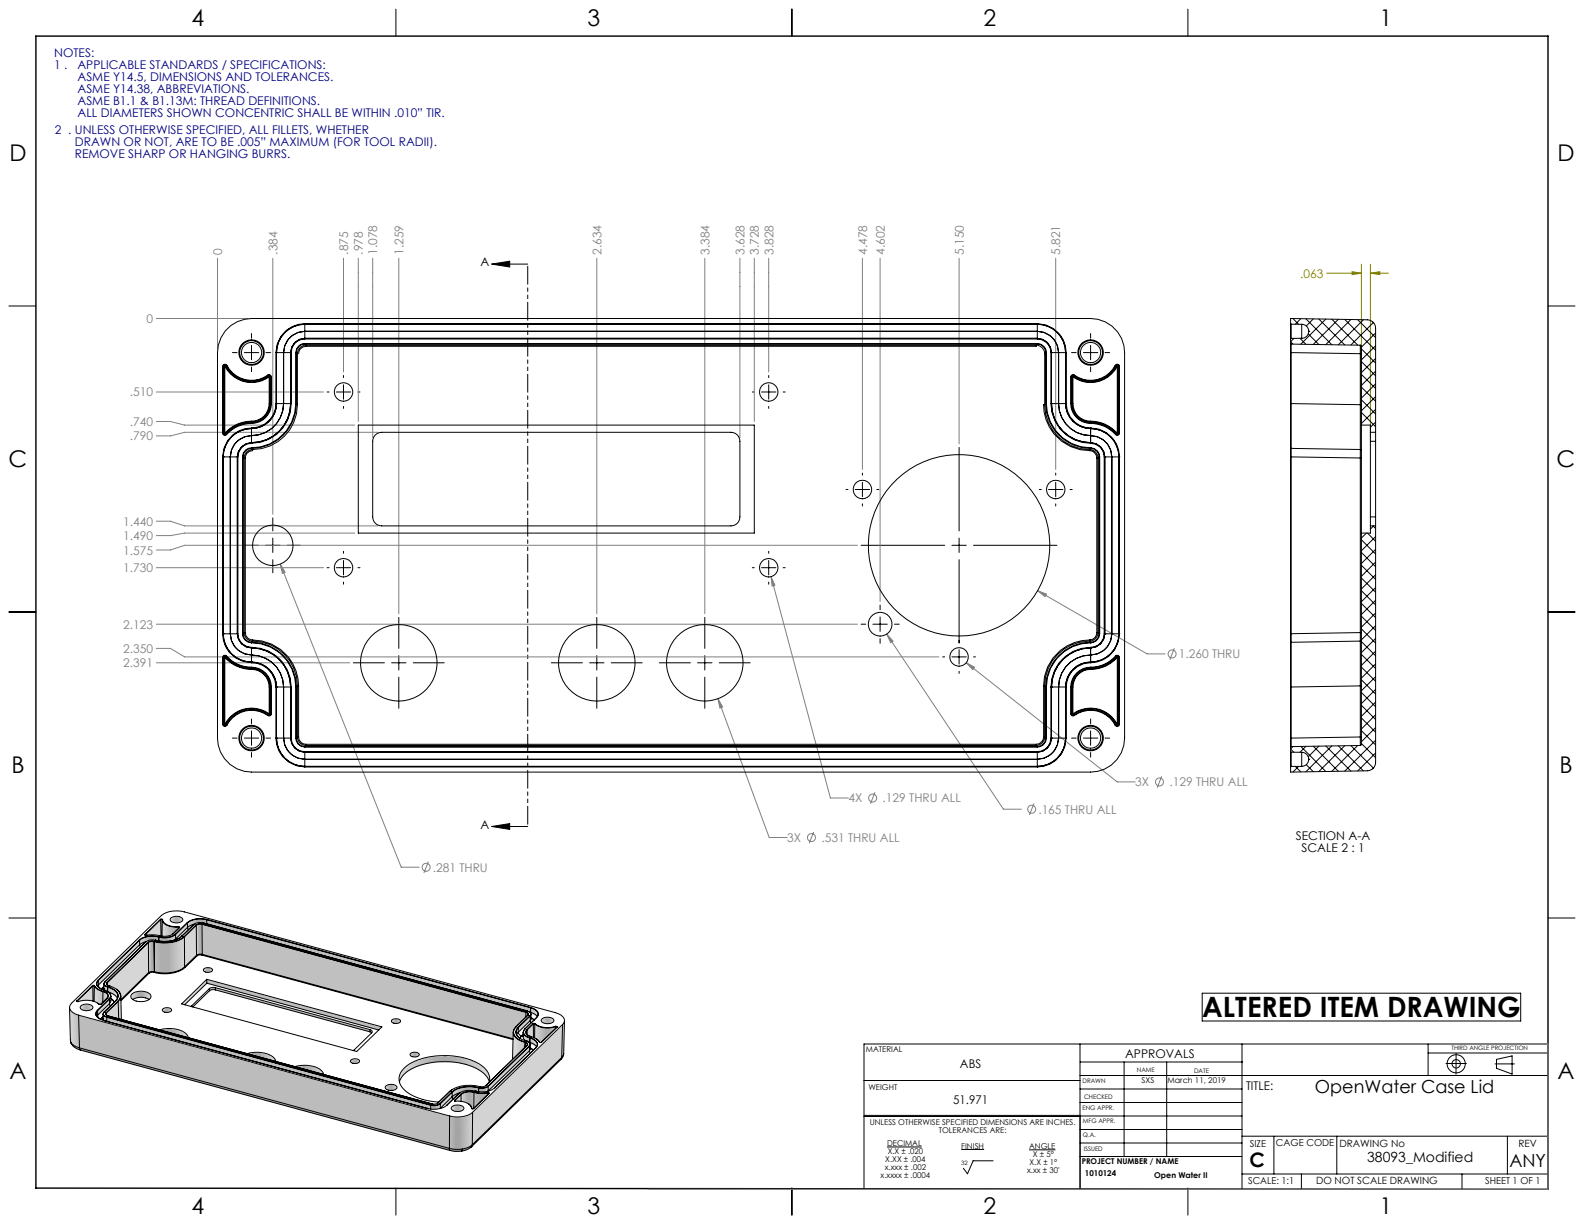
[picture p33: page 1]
TOLERANCES ARE:; CAGE CODE; DRAWING No; REV; 1.260 THRU; .129 THRU ALL; .531 THRU ALL; .281 THRU; .165 THRU ALL; SECTION A-A SCALE 2 : 1; SCALE: 1:1; DO NOT SCALE DRAWING; SHEET 1 OF 1; SXS March 11, 2019

NOTES:
1 . APPLICABLE STANDARDS / SPECIFICATIONS:
ASME Y14.5, DIMENSIONS AND TOLERANCES.
ASME Y14.38, ABBREVIATIONS.
ASME B1.1 & B1.13M: THREAD DEFINITIONS.
ALL DIAMETERS SHOWN CONCENTRIC SHALL BE WITHIN .010” TIR.
2 . UNLESS OTHERWISE SPECIFIED, ALL FILLETS, WHETHER
DRAWN OR NOT, ARE TO BE .005” MAXIMUM (FOR TOOL RADII).

REMOVE SHARP OR HANGING BURRS.

ALTERED ITEM DRAWING

THIRD ANGLE PROJECTION

OpenWater Case Lid

DRAWN
CHECKED
ENG APPR.
MFG APPR.
ISSUED
PROJECT NUMBER / NAME
1010124 Open Water II

UNLESS OTHERWISE SPECIFIED DIMENSIONS ARE INCHES.
DECIMAL
x.xxx ± .002
x.xxxx ± .0004

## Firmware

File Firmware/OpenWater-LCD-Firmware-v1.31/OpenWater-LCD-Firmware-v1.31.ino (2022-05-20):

/*************************************************************
 * OpenWater Turbidity Meter Code
 * Sheldon Stokes
 * Feb 22, 2019
 * 
 * Added serial code for bluno BLE.  The bluno acts as a wireless serial port
 * and the way I'm commuicating is via the DFB1 service
 * 
 * Byte                 Function
 * 0x00                 Collect Data
 * 0x01                 Read last measurement Mean
 * 0x02                 Read last measurement StDev
 * 0x03                 Read num averages
 * 0x04                 Read integration time
 * 0x05                 Read Slope
 * 0x06                 Read Intercept
 * 0x07                 Read mean counts
 * 0x08                 Read stdev counts
 * 0x09                 Read all above values in one sring
 * 0x10                 Read calibration date
 * 0x11                 Write calibration date
 * 0x12                 start Calibration
 * 0x13                 Read Cal Date Human Readable
 * 0x14                 Read Busy
 * 
 * 
 * In my BLE program you send commands as 01:0D for read last measurement mean
 * 
 *************************************************************/

// include the library code:
#include <EEPROM.h>
#include <Wire.h>
#include <TimeLib.h>
#include <Adafruit_RGBLCDShield.h>
#include <utility/Adafruit_MCP23017.h>

//********************Defines *************************
// These #defines make it easy to set the backlight color
#define RED 0x1
#define YELLOW 0x3
#define GREEN 0x2
#define TEAL 0x6
#define BLUE 0x4
#define VIOLET 0x5
#define WHITE 0x7

// ********************* EEPROM Stuff ******************

#define calSlopeAddress     0
#define calIntAddress       4
#define numAvesAddress      8
#define intTimeAddress      12
#define lowConcAddress      16
#define highConcAddress     24
#define debugActiveAddress  32
#define calDateAddress      36


//******************** variables **********************

Adafruit_RGBLCDShield lcd = Adafruit_RGBLCDShield();

#define RUNSTATE 0
#define CALSTATE 1
String versionNum = "1.31";

int det1Pin = 2;
int ledPin = 12;
int ledOnDelay = 2000;

int state,exitState;    

float calSlope, calInt;
int numDelaysForAve, debugActive;
float intTime, lowAct, highAct;
long calDate, bleDate;
long dStr1,dStr2,dStr3,dStr4;

float lowCnt, highCnt;
float stdDv, mean, stDevAcc,meanConc, stDevConc;

float lastReading, lastStDev;
volatile int takeReading = 0;
volatile int isBusy = 0;

volatile long cnt, dark,sig;

uint8_t buttons;

 
String str = "";
int len;


// date related variables
char out[25];
int calDay,calMonth,calYear,calHour,calMinute,calSecond;

void setup() {

  // load values from EEPROM
  EEPROM.get( calSlopeAddress, calSlope );
  EEPROM.get( calIntAddress , calInt );
  EEPROM.get( numAvesAddress , numDelaysForAve );
  EEPROM.get( intTimeAddress , intTime );
  EEPROM.get( lowConcAddress , lowAct );
  EEPROM.get( highConcAddress , highAct );
  EEPROM.get( debugActiveAddress, debugActive );
  EEPROM.get( calDateAddress, calDate);

  // trap blank EEPROM values
  if (isnan(calSlope)) calSlope= 1.0;
  if (isnan(calInt)) calInt = 0.0;  
  if (isnan(numDelaysForAve)) numDelaysForAve = 3;
  if (numDelaysForAve < 0) numDelaysForAve = 3;
  if (isnan(intTime)) intTime = 2.0; 
  if (isnan(lowAct)) lowAct  = 0.1; 
  if (isnan(highAct)) highAct = 1.0; 
  if (isnan(debugActive)) debugActive = 1;
  if (isnan(calDate)) calDate = 1583445767;

  Serial.begin(115200);   //this will start the serial port to talk through BLE on the bluno

  pinMode(LED_BUILTIN, OUTPUT);


  // setup IO pins
  pinMode(det1Pin, INPUT);
  pinMode(ledPin, OUTPUT);
  
  // set up the LCD's number of columns and rows: 
  lcd.begin(16, 2);
  lcd.setBacklight(WHITE);

  // pat ourselves on the back
  lcd.clear();
  lcd.setCursor(0,0);
  lcd.print("   OpenWater");
  lcd.setCursor(0,1);
  lcd.print("     v");
  lcd.print(versionNum);


  // set timer overflow interrupt for Bluetooth coms so it doesn't block when collecting data

  //set timer1 interrupt at 10Hz
  TCCR1A = 0;// set entire TCCR1A register to 0
  TCCR1B = 0;// same for TCCR1B
  TCNT1  = 0;//initialize counter value to 0
  // set compare match register for 5hz increments
  OCR1A = 1563;// = (16*10^6) / (10*1024) - 1 (must be <65536)
  // turn on CTC mode
  TCCR1B |= (1 << WGM12);
  // Set CS10 and CS12 bits for 1024 prescaler
  TCCR1B |= (1 << CS12) | (1 << CS10);  
  // enable timer compare interrupt
  TIMSK1 |= (1 << OCIE1A);


 // state = RUNSTATE;
  attachInterrupt(digitalPinToInterrupt(det1Pin), pulseISR, FALLING);

 
}  //setup

void loop() {


  buttons = lcd.readButtons();


  if ((buttons)||(takeReading)) {
      lcd.clear();
      lcd.setCursor(0,0);

      if ((buttons & BUTTON_SELECT)||(takeReading)) {       
          
          lcd.clear();
          while (buttons & BUTTON_SELECT) buttons = lcd.readButtons();    //wait for button to be released
          
          while (!(buttons & BUTTON_SELECT)&&(!takeReading)){


           buttons = lcd.readButtons();

           if (buttons & BUTTON_RIGHT) {
              exitState = CALSTATE;
              calDate++;      // add one second to existing calibration date to show a new cal happened
           }
           if (buttons & BUTTON_LEFT) exitState = RUNSTATE;
        
            
            lcd.setCursor(0,0);
            lcd.print(" Collect Data");
            lcd.setCursor(0,1);
            lcd.print(" Calibrate ");

            //clear edge
            lcd.setCursor(14,(exitState+1) & 0x1);
            lcd.print("  ");
            lcd.setCursor(14,exitState);
            lcd.print("<=");
            
          }  //while

          if (takeReading){
           // exitState = RUNSTATE;
            takeReading = 0;
          }

/******************************************************************************************
 **************           Cal State         ***********************************************
 ******************************************************************************************/

          if (exitState == CALSTATE){ 


            //************ calibration date routine *********************
            adjustCalDate();

            lcd.clear();
            lcd.print("Print Counts:"); 

            while (buttons & BUTTON_SELECT) buttons = lcd.readButtons();    //wait for button to be released           
            while (!(buttons & BUTTON_SELECT)){     // stay in loop until select button is pressed
              delay(250);
              buttons = lcd.readButtons();
              lcd.setCursor(0,1);
              if (debugActive == 1)  lcd.print("Yes");
              else lcd.print("No");
              lcd.print("   ");
              if(buttons & BUTTON_RIGHT) debugActive = 1;
              if(buttons & BUTTON_LEFT) debugActive = 0;
            }
            EEPROM.put(debugActiveAddress,debugActive);



/**********************************************/


            lcd.clear();
            lcd.print("Num Averages:"); 


            while (buttons & BUTTON_SELECT) buttons = lcd.readButtons();    //wait for button to be released           
            while (!(buttons & BUTTON_SELECT)){     // stay in loop until select button is pressed
              delay(250);
              buttons = lcd.readButtons();
              lcd.setCursor(0,1);
              lcd.print(numDelaysForAve);
              lcd.print("   ");
              if(buttons & BUTTON_RIGHT) numDelaysForAve += 1;
              if(buttons & BUTTON_LEFT) numDelaysForAve -= 1;
            }
            EEPROM.put(numAvesAddress,numDelaysForAve);


/**********************************************/

  
            lcd.clear();
            lcd.print("Int Time:"); 


            while (buttons & BUTTON_SELECT) buttons = lcd.readButtons();    //wait for button to be released           
            while (!(buttons & BUTTON_SELECT)){     // stay in loop until select button is pressed
              delay(100);
              buttons = lcd.readButtons();
              lcd.setCursor(0,1);
              lcd.print(intTime);
              lcd.print("   ");
              if(buttons & BUTTON_RIGHT) intTime += 0.1;
              if(buttons & BUTTON_LEFT) intTime -= 0.1;
            }
            EEPROM.put( intTimeAddress , intTime );


/**********************************************/
          
            
            lcd.clear();
            lcd.print("1st Soln Conc:"); 
  
          
            while (buttons & BUTTON_SELECT) buttons = lcd.readButtons();    //wait for button to be released           
            while (!(buttons & BUTTON_SELECT)){     // stay in loop until select button is pressed
              delay(100);
              buttons = lcd.readButtons();
              lcd.setCursor(0,1);
              lcd.print(lowAct);
              if(buttons & BUTTON_RIGHT) lowAct += 0.1;
              if(buttons & BUTTON_LEFT) lowAct -= 0.1;
            }
            EEPROM.put( lowConcAddress , lowAct );

            
            //****************** collect data here ****************************
            collectData();
            lowCnt = sig-dark;
            

/**********************************************/



            lcd.clear();
            lcd.print("2nd Soln Conc:");   
          
            while (buttons & BUTTON_SELECT) buttons = lcd.readButtons();    //wait for button to be released           
            while (!(buttons & BUTTON_SELECT)){     // stay in loop until select button is pressed
              delay(100);
              buttons = lcd.readButtons();
              lcd.setCursor(0,1);
              lcd.print(highAct);
              if(buttons & BUTTON_RIGHT) highAct += 0.1;
              if(buttons & BUTTON_LEFT) highAct -= 0.1;
            }
            EEPROM.put( highConcAddress , highAct );
            
            //****************** collect data here ****************************
            collectData();
            highCnt = sig-dark;




            //****************** calculate coefficients ***********************

            calSlope = (highAct - lowAct) / (highCnt - lowCnt);
            calInt = lowAct - (calSlope * lowCnt);
            
            EEPROM.put( calSlopeAddress, calSlope );
            EEPROM.put( calIntAddress , calInt );


          // add cal date
          //  EEPROM.put( calDateAddress, calDate);
          putCalDate();
            
                  
          } //calcase


/******************************************************************************************
 **************           Run State         ***********************************************
 ******************************************************************************************/


          if (exitState == RUNSTATE){  

            isBusy = 1;
            collectData();

        // calculate the mean and stDev concentration


//            stDevAcc = 0;
//            meanConc = ((sig-dark) * calSlope) + calInt;
//            for (int i = 0; i < numDelaysForAve; i++)
//            {
//              stDevAcc += sq((((readings[i]-dark) * calSlope) + calInt) - meanConc) ; 
//            }
//            stDevConc = sqrt(stdevAcc/numDelaysForAve);

            lcd.clear();
            lcd.print("Reading:");
            lcd.setCursor(0,1);            
            lcd.print(((sig-dark) * calSlope) + calInt);

//            Serial.print(sig);
//            Serial.print(",");
//            Serial.print(mean);
//            Serial.print(",");
//            Serial.print(dark);
//            Serial.print(",");
//            Serial.print(((sig-dark) * calSlope) + calInt);           
//            
//            lcd.print(meanConc);
            lcd.setCursor(8,1);
            lcd.print(stdDv*calSlope);

            lastReading = ((sig-dark) * calSlope) + calInt;
            lastStDev = stdDv*calSlope;

            isBusy = 0;
            // convert to conc

            
          }  //runstate




      }
    }


}  //loop



void pulseISR() {
  cnt++;
}
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

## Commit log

2022-05-10 Adding mechanical design files.
    [SLA-Sample-Well-Hinge.STEP, SLA-Sample-Well-Lid.STEP, SLA-Sample-Well.STEP]
2022-05-18 Adding BOM.
    [T03_Prototype_BOM.xlsx]
2022-05-18 Adding schematic for laser control circuit.
2022-05-26 Adding diameter to hole for reed switch.
2022-05-27 Changing BOM to pdf format.
    [T03_Prototype_BOM.xlsx]
2022-05-27 Adding license link to Arduino Time library.
2022-05-29 Updating assembly instructions.
2022-05-29 Adding link to bill of materials in ReadMe.
2022-05-29 Adding Adafruit LCD assembly instructions.
2022-05-29 Adding instructions to rename Bluetooth device.
2022-05-29 Adding photo of assembled case lid.
